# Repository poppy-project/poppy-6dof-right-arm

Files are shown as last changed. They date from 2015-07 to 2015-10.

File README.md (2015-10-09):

# Poppy Right Arm (WORK IN PROGRESS!)

Watch PoppyRightArm in action! :

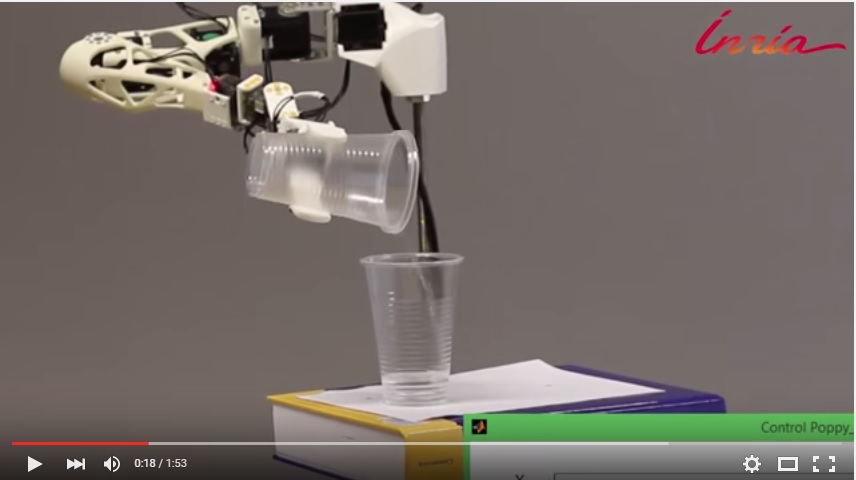
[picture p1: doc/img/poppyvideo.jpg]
Little red ridning hood (https://www.youtube.com/watch?v=47-JBuZhTWU&feature=youtu.be "Little red riding hood - Click to Watch!")


## [Documentation »](https://github.com/poppy-project/poppy-6dof-right-arm/blob/master/doc/README.md)
## [STL View »](doc/stl/PoppyRightArm.STL)

## Credit

The beginning of this project was inspired from the project [Poppy Humanoid](https://www.poppy-project.org/?lang=fr). This project was conceived to simulate an upper limb prostheses. In this [link](https://vimeo.com/134840606) you can watch an EMG control of Poppy Humanoid where this projectt will replace all Poppy humanoid to use only the part of interest, and in this other [link](https://github.com/joelortizsosa/EMG_Processing) you can dowload the software used in the video

This project is in charge of the research center [INRIA](http://www.inria.fr/centre/bordeaux) in collaboration of [INCIA](http://www.incia.u-bordeaux1.fr/)

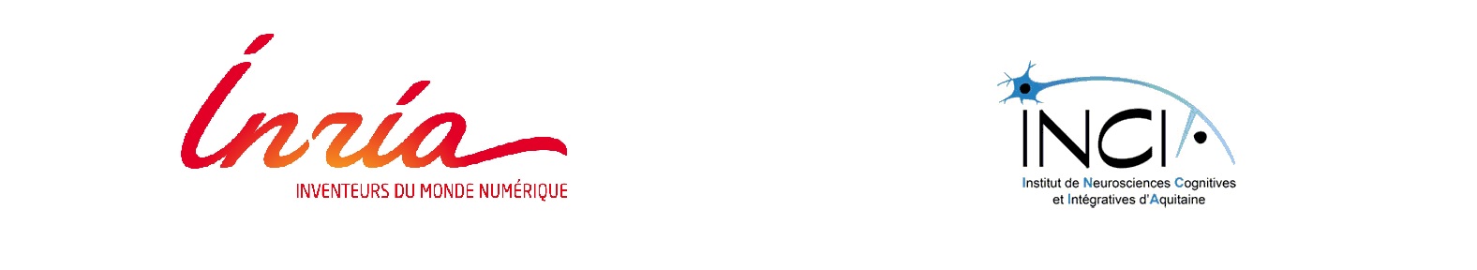
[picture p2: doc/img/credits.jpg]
credits


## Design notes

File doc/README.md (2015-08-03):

# Poppy Right Arm documentation

<p align="center">
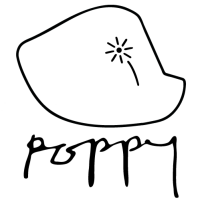
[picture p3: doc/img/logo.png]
Poppy_logo.

</p>

In this documentation you will find everything you need to assemble your own arm from scratch:

## [Assembly »]( https://github.com/poppy-project/poppy-6dof-right-arm/blob/master/doc/assembly.md)

In this section we explain, how you can assembly all the hadware ....

## [Electronic »]( https://github.com/poppy-project/poppy-6dof-right-arm/blob/master/doc/electronic.md)

In this section we explain, how you can power up all the motors ....

## [Software »]( https://github.com/poppy-project/poppy-6dof-right-arm/blob/master/doc/software.md)

In this section we explain, how you can install the creature necessary to control Poppy_Right_Arm, and we show some applications  ....

## [Common Bug »]( https://github.com/poppy-project/poppy-6dof-right-arm/blob/master/doc/common_Bug.md)

If you have any trouble when you execute your code, you can try watch this section ...

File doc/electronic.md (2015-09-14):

# About the Electronic

A small bit of electronic hacking is required for now. You need to power the XL-320 motors with 7.5V and the MX-28 with 12V.

The cables between motors have two purposes:

* Distribute alimentation to each motor
* Convey messages to each motor (ordering them to move or asking them for sensors values)

Thus the alimentation should be added between the USB2AX (that deals with communication aspects) and the motors.
To this end simply create the following card that can power both type of motors.

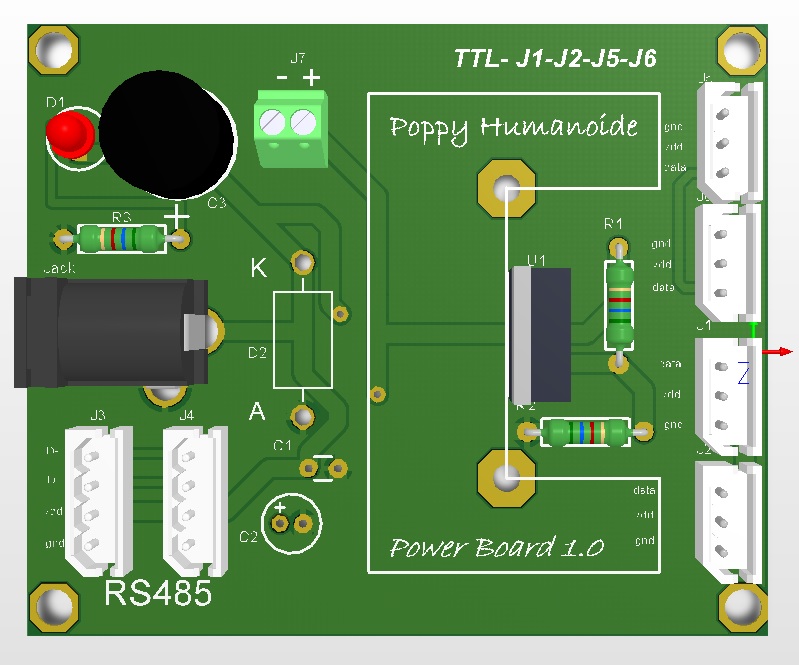
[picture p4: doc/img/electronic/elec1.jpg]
elec1


## Bill of Materials

| Description                   | Designator | Quantity |
| -----------------------------:|:----------:|:--------:|
| [CAP CER 0.1UF 50V RADIAL](http://fr.farnell.com/kemet/c320c104m5u5ta/condensateur-mlcc-z5u-100nf-50v/dp/1457658)      |    C1      |     1    |          
| [CAP ALUM 1.0UF 50V RADIAL](http://fr.farnell.com/nichicon/ukw1h010mdd1td/aluminum-electrolytic-capacitor/dp/1823811)     |    C2      |     1    |
| [Cap Aluminum Lytic 1000uF 25V](http://fr.farnell.com/panasonic-electronic-components/eca1ehg102/condensateur-elec-alu-1000uf-25v/dp/1848543) |    C3      |     1    |
| [Standard LED](http://fr.farnell.com/vishay/tlur4400/led-3mm-rouge/dp/1045372)                  |    D1      |     1    |
| [1N5822](http://fr.farnell.com/multicomp/1n5822/diode-schottky-3a-40v/dp/7429339)                        |    D2      |     1    |
| [Molex 22-03-5035](http://fr.farnell.com/molex/22-03-5035/embase-droite-2-5mm-3-voies/dp/9979620?ost=Molex+22-03-5035)              |   J1,J2    |     2    |
| [Molex 22-03-5045](http://fr.farnell.com/molex/22035045/embase-vertical-2-5mm-4-voies/dp/1104204?ost=Molex+22-03-5045)              |   J3,J4    |     2    |
| [Molex 53253-0370](http://fr.farnell.com/molex/53253-0370/embase-male-2-0mm-3-voies/dp/1756921?ost=Molex+53253-0370)              |   J5,J6    |     2    | 
| [CONN 2POS 1725656](http://fr.farnell.com/phoenix-contact/1725656/bornier-sur-ci-2v-2-54mm/dp/3041359?ost=Phoenix+Contact+1725656)             |    J7      |     1    |
| [CONN PWR JACK  PJ-202AH](http://fr.farnell.com/switchcraft/rapc712bk/connector-dc-power-jack-5a/dp/1617204?CMP=os_Google-FR_ProductDetail_Redirect)       |   JACK     |     1    |
| [Resistors 200Ohm 1/4W](http://fr.farnell.com/multicomp/mcmf0w4ff2000a50/metal-film-resistor-200-ohm-250mw/dp/1126948)         |    R1      |     1    |
| [Resistors 1KOhm 1/4W](http://fr.farnell.com/multicomp/mcmf0w4ff1001a50/metal-film-resistor-1kohm-250mw/dp/1126919)          |    R2      |     1    |
| [Resistors 430Ohm  1/4W](http://fr.farnell.com/multicomp/mcmf0w4ff4300a50/metal-film-resistor-430-ohm-250mw/dp/1129150)        |    R3      |     1    |
| [Adjuste Regulator LM317](http://fr.farnell.com/stmicroelectronics/lm317t/regulateur-ajust-1-2-37v-to-220/dp/9756027)       |    U1      |     1    |
| [H/SINK 6396B](http://fr.farnell.com/aavid-thermalloy/6396bg/dissipateur-to-220-218-5-6c-w/dp/1213472?ost=6396B)| TO-220 radiator |   1  |
The card design has been made in CircuitMaker, you can open the project in:

[https://workspace.circuitmaker.com/Account/Login?ReturnUrl=%2fProjects%2f5513C8C5-B3C1-4E83-8C02-FD9805562557] (https://workspace.circuitmaker.com/Account/Login?ReturnUrl=%2fProjects%2f5513C8C5-B3C1-4E83-8C02-FD9805562557)

But you need an account, you can create an account in this [link](http://www.circuitmaker.com/thank-you/#download), then you have access to project.

If you have your own PCB designer for make circuits, you can follow this schematic:

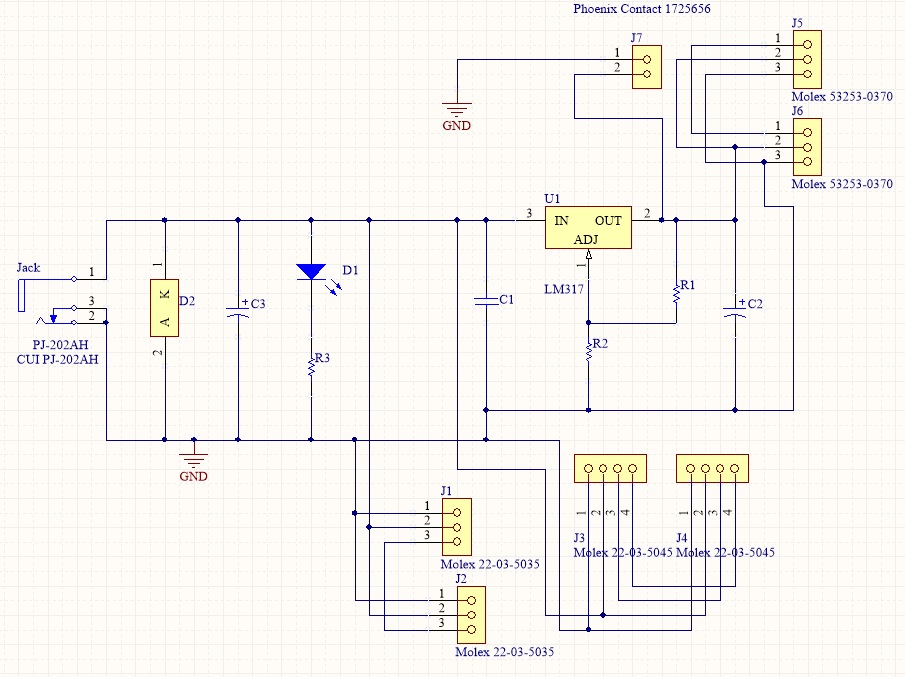
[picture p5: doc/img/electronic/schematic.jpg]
schematic


## [Software »]( https://github.com/poppy-project/poppy-6dof-right-arm/blob/master/doc/software.md)

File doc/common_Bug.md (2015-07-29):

# Error in voltage

The voltage for the XL-320 is configured at 7.4V in pypot, if the source power has more voltage, pypot detect:

  **NotImplementedError**

The dynamixel XL-320 supports up to 8 volts, so we can modify the library to correct this error, because when this 
error appears, the motors stop working.

we need to find the file error.py, usually found in:

 *C:\Python27\Lib\site-packages\pypot\dynamixel\error.py*
 
Then we comment the line 52, and we add the sentence "pass", like the image below:

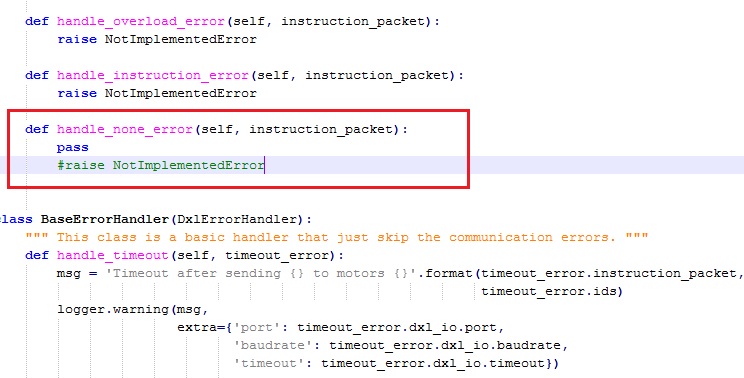
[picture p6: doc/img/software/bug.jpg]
bug


With this modification we can control the motors without any inconvenience

## [Home »] (https://github.com/joelortizsosa/Poppy_Right_Arm_Creature/blob/master/doc/README.md)

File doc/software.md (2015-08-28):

# About the Software

## Install Creature

you can donwload the creature in this [link](https://github.com/poppy-project/poppy-6dof-right-arm/archive/master.zip).To make the installation (in windows xp,7,8), It's necessary load  the command-line interpreter on Windows and then 
you need to be located in the folder of the creature:

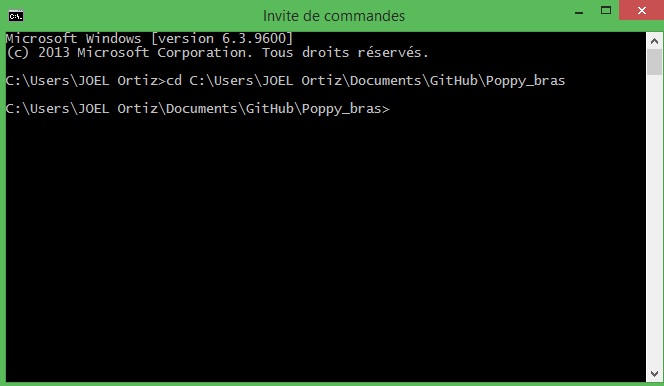
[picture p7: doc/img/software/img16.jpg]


Then you can install the library as follows

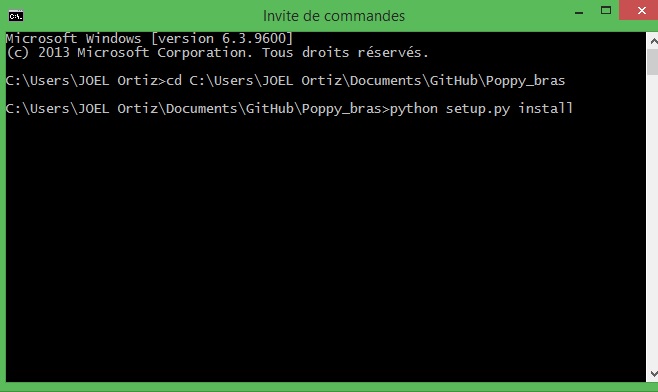
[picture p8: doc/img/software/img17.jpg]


*If you dont have python and the software necessay already installed, you can follow these [instructions](https://forum.poppy-project.org/t/poppy-on-windows-all-you-need-to-do/392)*

## Configuration of *.JSON

As the gripper of the arm can be configured to add different degrees of freedom, it is necessary to disable / enable the motors to be used. To do this you need to modify the configuration file, located at:

*C:\Python27\Lib\site-packages\poppy_right_arm-1.0.0-py2.7.egg\poppy_right_arm\configuration\poppy_right_arm.json*

Then you can open this file with the Notepad

* if you write "true", the motor will be disabled.

* if you write "false", the motor will be enabled.

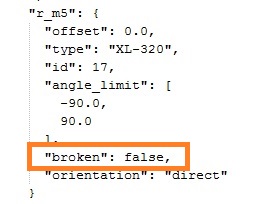
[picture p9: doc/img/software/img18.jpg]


> *Note: change the file. * json in Poppy_Right_Arm not cause bug in any others creatures*

Once these parameters are defined, now we can use the creature.

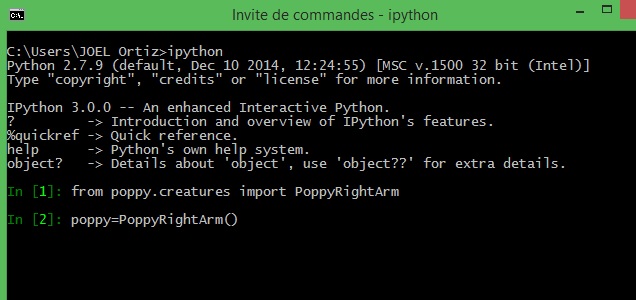
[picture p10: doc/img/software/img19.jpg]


## Python Server

To control the Poppy_Right_Arm from another software such as Matlab, you must create a server in python that can handle all the motors remotely.

We can start an HTTP server permitting the remote access of  Poppy_Right_Arm creature. In this [link](https://github.com/poppy-project/pypot/blob/master/samples/notebooks/Accessing%20pypot%20REST%20API%20through%20HTTP%20requests.ipynb) you can find one explanation. Extra [information](https://github.com/poppy-project/pypot/blob/master/REST-APIs.md).

**Note: Poppy_Right_Arm creature use a software architecture style for building scalable web services (REST-API)*

we implemented a server, with the ideal setting to control the Poppy_Right_Arm. You can see the code in this [link] (https://github.com/poppy-project/poppy-6dof-right-arm/blob/master/applications/HTTP_server/Poppy_Right_Arm_Server.py)
To execute the server it's necessary load  the command-line interpreter and to be located in the folder of the code, then you put this code:

**python Poppy_Right_Arm_Server.py**

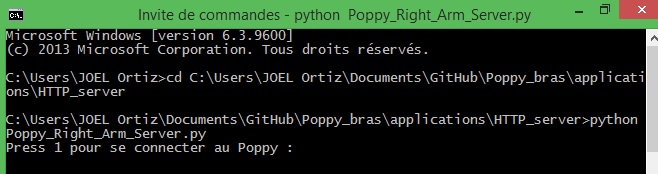
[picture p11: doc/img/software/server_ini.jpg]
server_ini


*Note: if you have saved the code with another name, it is necessary to run with that name*

## Matlab Control

With the python server we can do different applications, for example we used matlab to calculate the inverse kinematics to control the arm, for do it, we use the calcule of this [link](https://forum.poppy-project.org/t/cinematique-inverse-bras-de-poppy/1306)

There are many software with [REST API](https://en.wikipedia.org/wiki/Representational_state_transfer) support, Matlab only support REST API from 2014 version, but we can use the HTTP protocol. The HTTP protocol implemented in Matlab is very basic, you can download an improved version in this [link](http://www.mathworks.com/matlabcentral/fileexchange/35693-urlread2)

We did a client in matlab that you can download from this [link](https://github.com/poppy-project/poppy-6dof-right-arm/raw/master/applications/Matlab_client/Matlab_client.rar). This client can control the Poppy_Right_Arm using the inverse kinematics, only you have to press the boton "Connect" and then move the sliders of each axe.

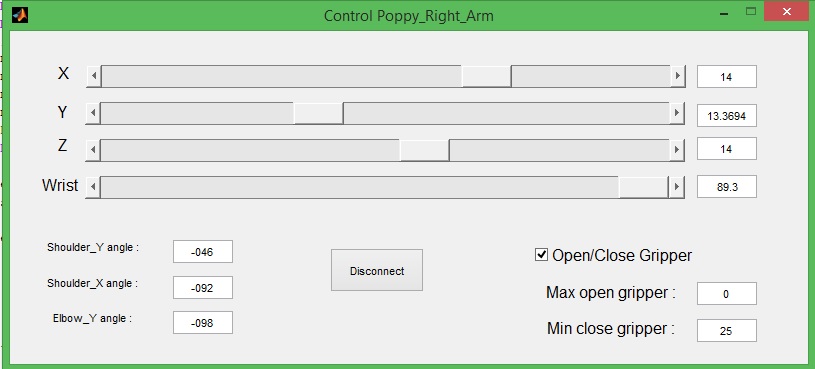
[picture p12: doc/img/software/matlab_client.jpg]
matlab_client


We developed the same sotware in python, using PyQT4, you can access in this [link](https://github.com/joelortizsosa/Inverse-Kinematic-Python)

## [Home »] (https://github.com/poppy-project/poppy-6dof-right-arm/blob/master/doc/README.md)

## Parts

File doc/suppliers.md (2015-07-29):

# List of Suppliers

## Robotics

### OLLO

* Ollo rivets: http://www.generationrobots.com/en/401870-ollo-rivet-set-ors-10.html?search_query=OLLO&results=11

### Dynamixel

* XL320: http://www.generationrobots.com/en/401692-dynamixel-xl-320-servo-motor.html
* MX-28: http://www.generationrobots.com/fr/401080-servomoteur-dynamixel-mx-28t.html?search_query=MX-28T&results=15

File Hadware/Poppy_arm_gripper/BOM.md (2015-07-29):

| Part Name       | Quantity |   Note   |
| ---------------:|:--------:|:--------:|
| Shift_one_side  |    2     |          |
| forearm         |    1     |          |
| morceau_1       |    1     |          |
| morceau_2       |    1     |          |
| shoulder        |    1     |          |
| supp_gripper    |    1     |          |
| supp_1          |    2     |          |
| supp_2          |    1     |          |
| supp_3          |    1     | Optional |
| supp_bras_droit |    1     |          |
| supp_for_table  |    1     |          |
| upper_arm       |    1     |          |

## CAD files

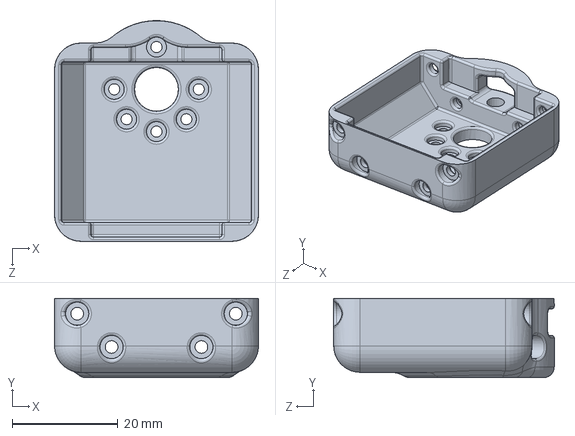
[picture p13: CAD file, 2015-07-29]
Hadware/Poppy_arm_gripper/Components/shoulder.SLDPRT
38.6 x 15.0 x 41.7 mm

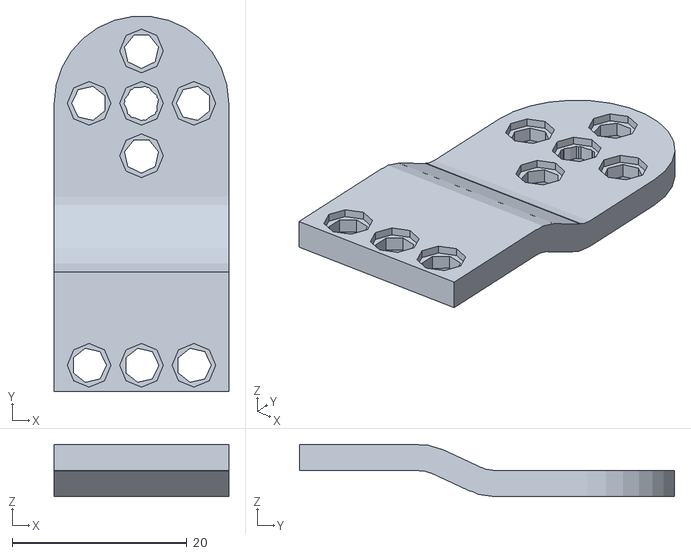
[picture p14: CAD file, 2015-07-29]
Hadware/Poppy_arm_gripper/Components/STL/shift_one_side.stl
20.0 x 42.9 x 6.00

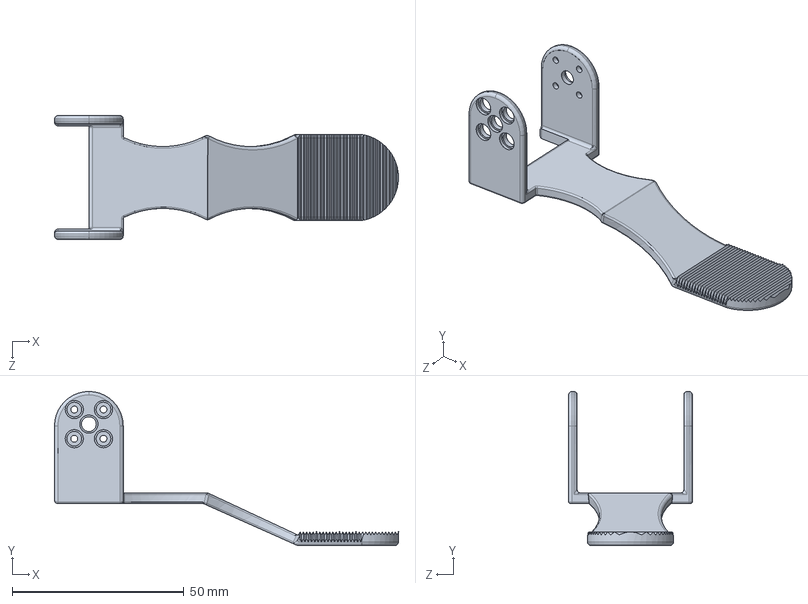
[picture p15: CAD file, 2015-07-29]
Hadware/Poppy_arm_gripper/Components/morceau_2.SLDPRT
100.0 x 44.8 x 36.0 mm

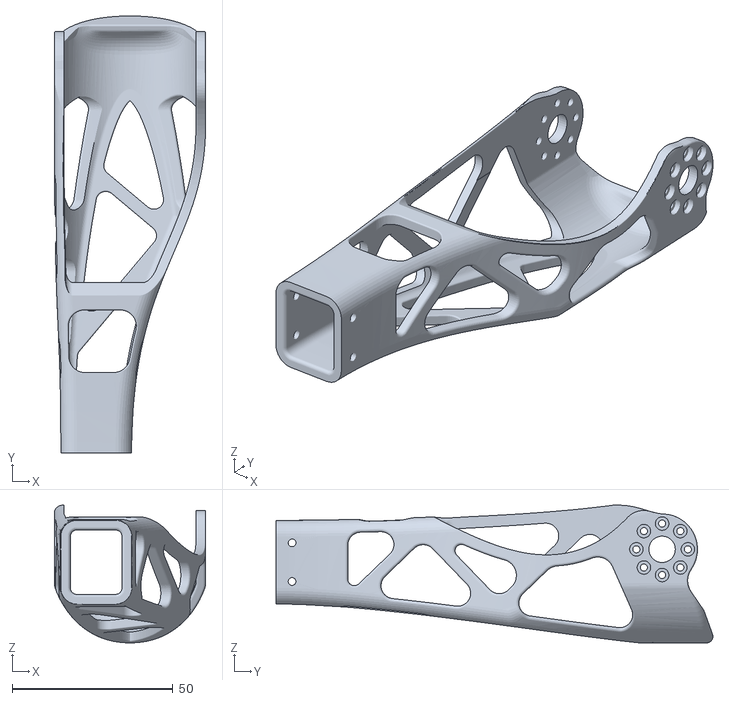
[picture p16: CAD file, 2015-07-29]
Hadware/Poppy_arm_gripper/Components/STL/forearm.STL
47.0 x 135.8 x 42.8

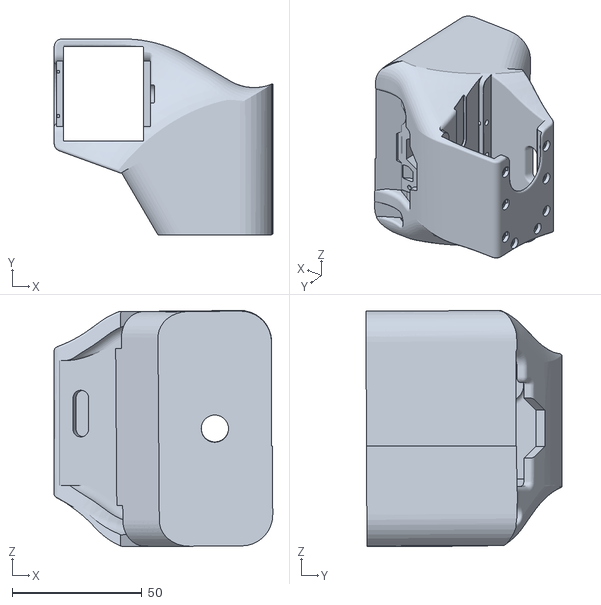
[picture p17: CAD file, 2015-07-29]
Hadware/Poppy_arm_gripper/Components/STL/support_Bras_droit_mod1.STL
84.2 x 75.6 x 90.9

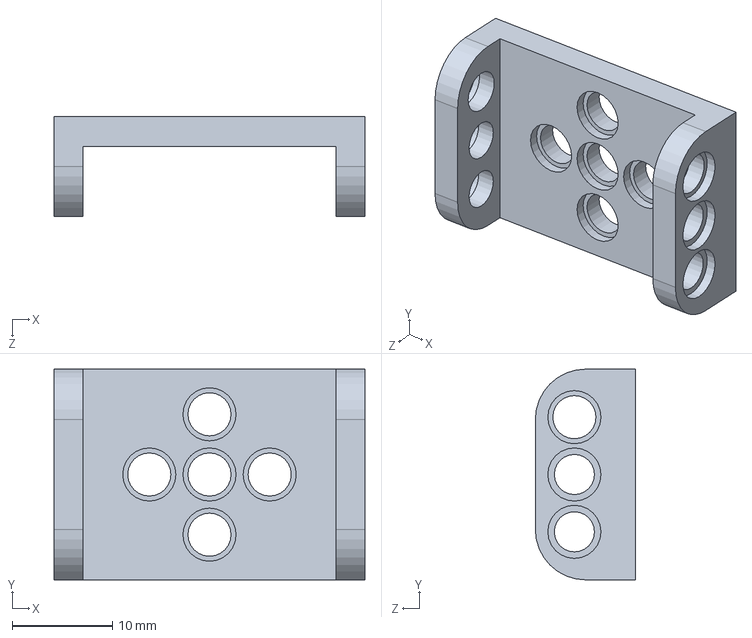
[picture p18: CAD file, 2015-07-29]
Hadware/Poppy_arm_gripper/Components/supp_1.SLDPRT
31.0 x 21.0 x 10.0 mm

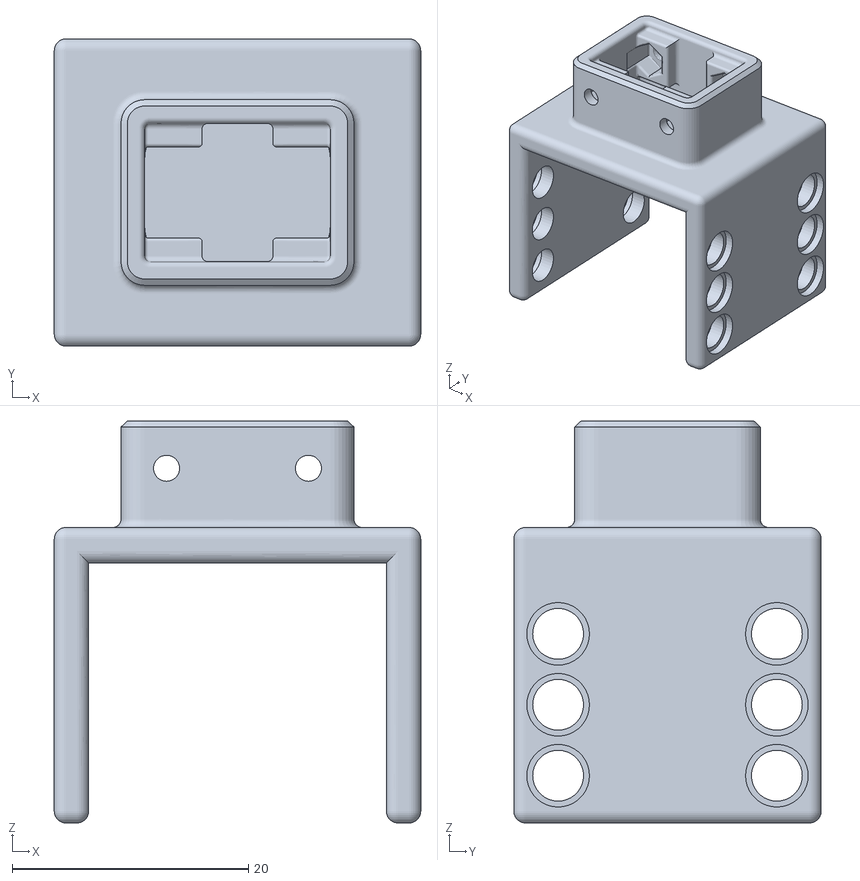
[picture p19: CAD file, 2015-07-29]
Hadware/Poppy_arm_gripper/Components/STL/support_gripper.STL
31.0 x 26.0 x 34.0

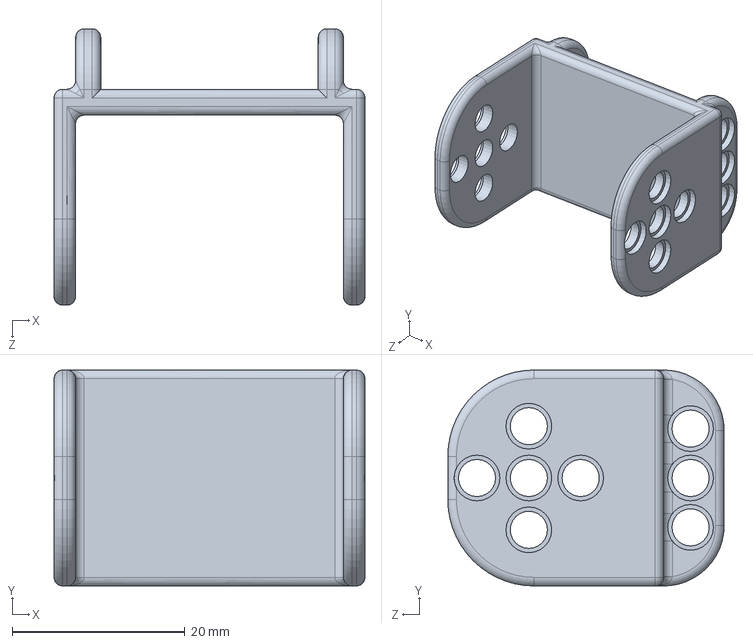
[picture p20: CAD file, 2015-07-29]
Hadware/Poppy_arm_gripper/Components/supp_3.SLDPRT
36.0 x 25.0 x 32.0 mm

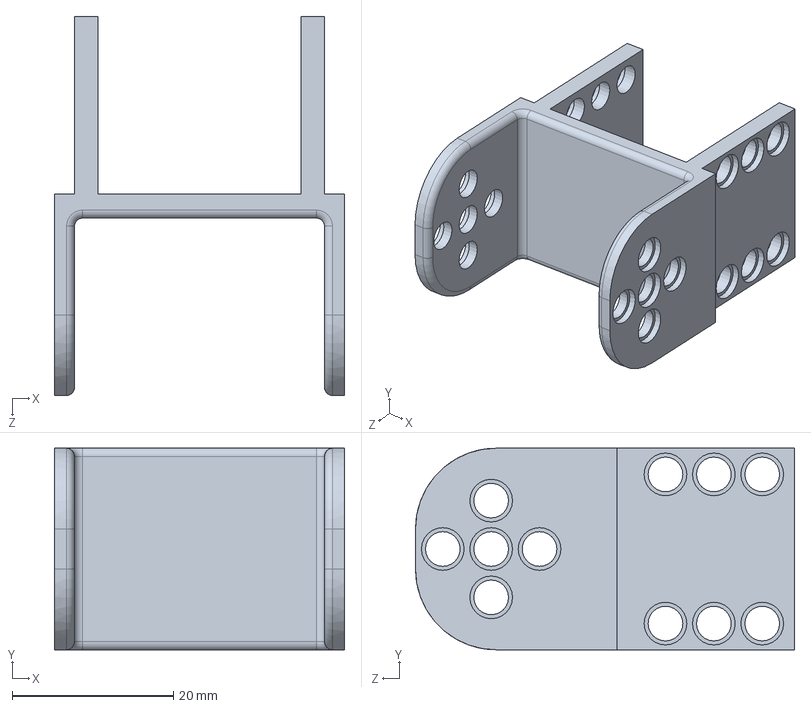
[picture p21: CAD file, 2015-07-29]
Hadware/Poppy_arm_gripper/Components/supp_2.SLDPRT
36.0 x 25.0 x 47.0 mm

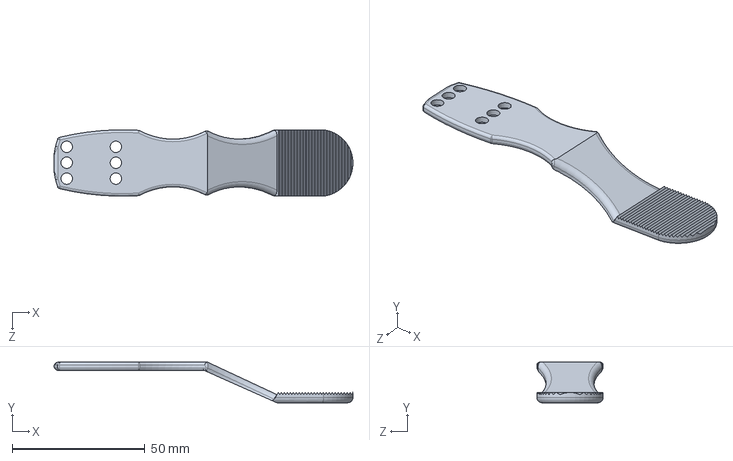
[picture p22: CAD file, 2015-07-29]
Hadware/Poppy_arm_gripper/Components/morceau_1.SLDPRT
112.6 x 15.3 x 25.0 mm

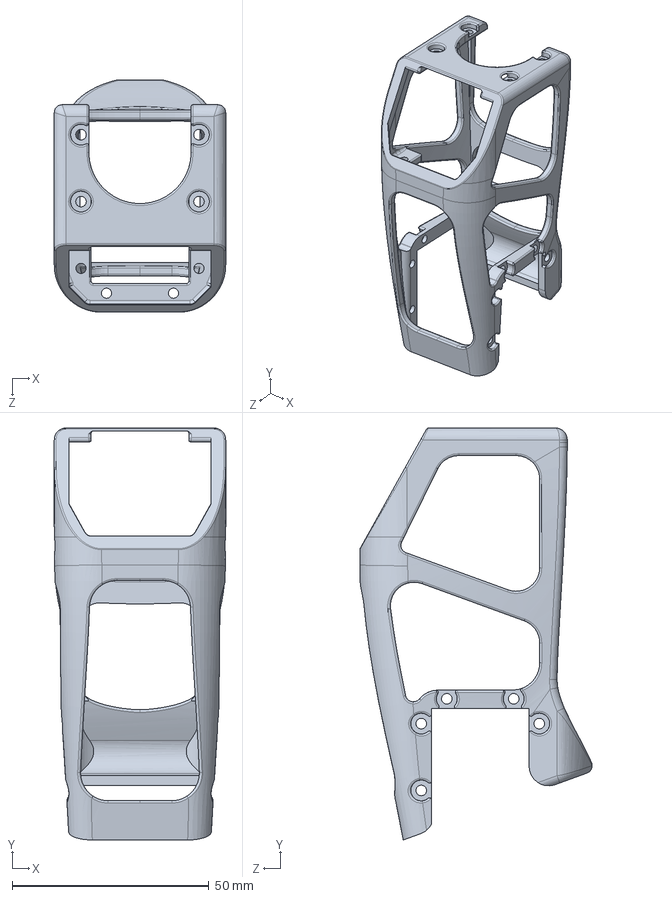
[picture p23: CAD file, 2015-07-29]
Hadware/Poppy_arm_gripper/Components/upper_arm.SLDPRT
43.6 x 104.7 x 59.1 mm

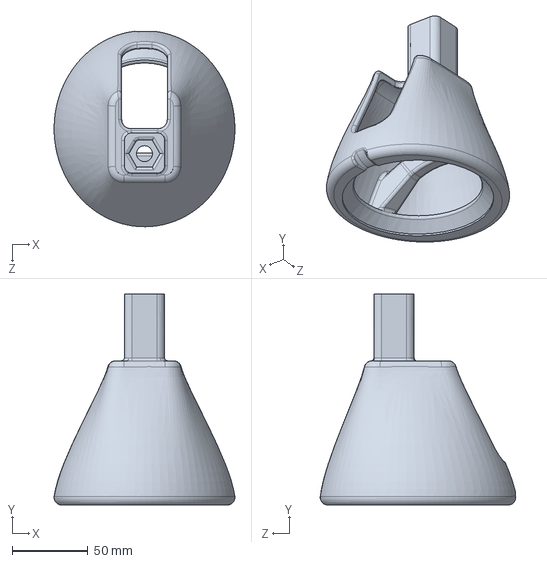
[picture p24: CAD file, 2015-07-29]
Hadware/Poppy_arm_gripper/Components/support_for_table.SLDPRT
119.1 x 139.0 x 128.8 mm

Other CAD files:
Hadware/Poppy_arm_gripper/Components/STL/morceau_1.STL
Hadware/Poppy_arm_gripper/Components/STL/morceau_2.STL
Hadware/Poppy_arm_gripper/Components/STL/shoulder.STL
Hadware/Poppy_arm_gripper/Components/STL/supp_1.STL
Hadware/Poppy_arm_gripper/Components/STL/supp_2.STL
Hadware/Poppy_arm_gripper/Components/STL/supp_3.STL
Hadware/Poppy_arm_gripper/Components/STL/support_for_table.STL
Hadware/Poppy_arm_gripper/Components/STL/upper_arm.STL

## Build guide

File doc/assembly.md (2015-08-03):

# Step by Step Assembly

## BOM

For building a Poppy right Arm, you will need:

* 5x robotis [XL-320] (http://www.generationrobots.com/en/401692-dynamixel-xl-320-servo-motor.html?search_query=OLLO&results=23)
* 10x [XL cable](http://www.generationrobots.com/en/402090-3p-130-mm-cables-for-xl-servos-x5.html)
* 2x [USB2AX] (http://www.generationrobots.com/en/401584-usb2ax-for-dynamixel-servos.html?search_query=usb2aX&results=5)
* 4x robotics [MX-28] (http://www.generationrobots.com/en/401080-dynamixel-mx-28t-actuator-robotis.html?search_query=MX-28T&results=15)
* 2x HN07-I101 [Horn](http://www.generationrobots.com/en/400939-hn07-i101-horn-and-bearing-set-for-dynamixel-actuators-robotis.html)
* 1x FR07-H101K [Set] (http://www.generationrobots.com/en/400917-fr07-h101k-set-robotis.html?search_query=FR07-H101K&results=2)
* 1x [TTL cable](http://www.generationrobots.com/en/401739-3p-cable-set-bcs-3p01-for-dynamixel-servo-motors.html?search_query=mx+cable&results=336)
* 1x small electronic board (see the [electronic section](electronic.md))
* 1x [Power Supply 12V - 5A] (http://www.trossenrobotics.com/p/power-supply-12vdc-5a.aspx)
* the 3D printed parts: [STL] (https://github.com/joelortizsosa/Poppy_bras_Creatures/releases) [BOM](https://github.com/joelortizsosa/Poppy_bras_Creatures/blob/master/Hadware/Poppy%20bras%20prehenseur/BOM.md)
* 1x [threaded shaft](http://www.leroymerlin.fr/v3/p/produits/tige-filetee-en-acier-zingue-long-1-m-x-diam-10-mm-e54322) D:10mm L: min 45 cm
* 4x [Hex Nut](http://www.vis-express.fr/fr/ecrous-inox-a2-hu/19735-ECROU-HEXAGONAL-M10-INOX-DACROMET-8425001057.html) D:10 mm
* 1x [OLLO Pulley-L](http://www.generationrobots.com/en/401871-ollo-pulley-l-gray-5pcs.html?search_query=OLLO&results=23) and their rivets
* many [OLLO rivets](http://www.generationrobots.com/en/401870-ollo-rivet-set-ors-10.html)
* 1x [OLLO Tool](http://www.generationrobots.com/en/401872-ollo-tool.html)
* 1x[100mm with lever arm suction pad](http://www.ventouses-soufflets.com/ventouses-avec-levier-d-appui/54-ventouse-100mm-avec-levier-d-appui-et-avec-patte-de-fixation-noire.html)
* 2x M5 nuts
* 2X M5x20mm screws
* 4x Bolt PHS M2x6 
* 4x N1 Nut M2 

### Visserie Optional:
* 1x Wrench Bolt M2.5*6 (200 pcs)
* 1x Nut M2.5 (400 pcs)

## Assembling your robot

## Step 1

First for assambly the poppy right arm we can use poppy basic arms [Doc] (https://github.com/poppy-project/Poppy-basic-arms/blob/master/doc/right_arm_assembly_instructions.md)

## Step 2
Mount the arm of step 1, motor MX-28, FR07 and threaded shaft on the 3D printed suppport.

Always align the horn with the motor before assembling them (red circle)

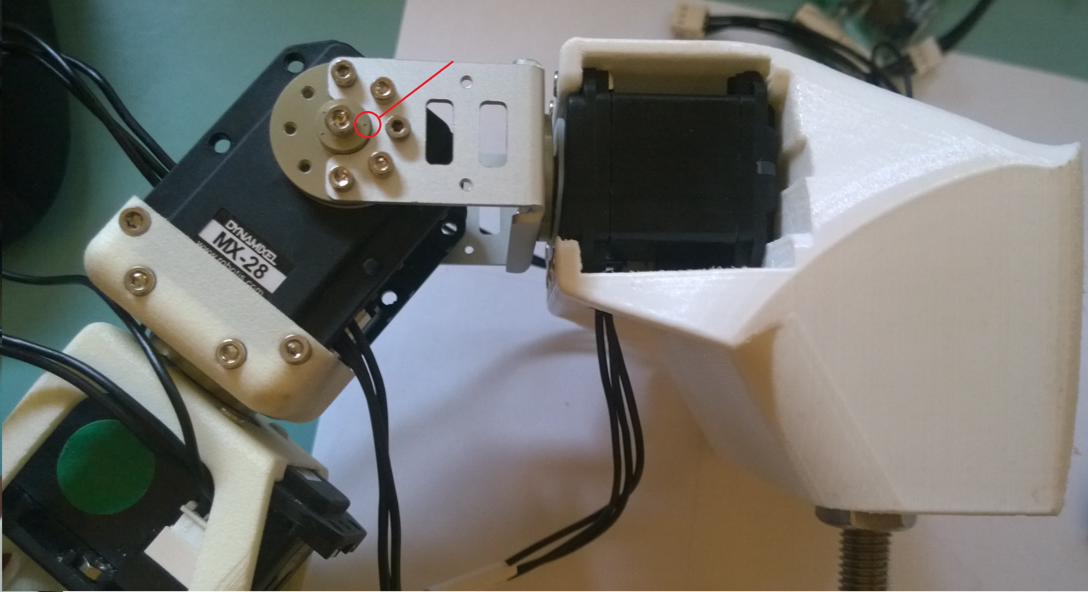
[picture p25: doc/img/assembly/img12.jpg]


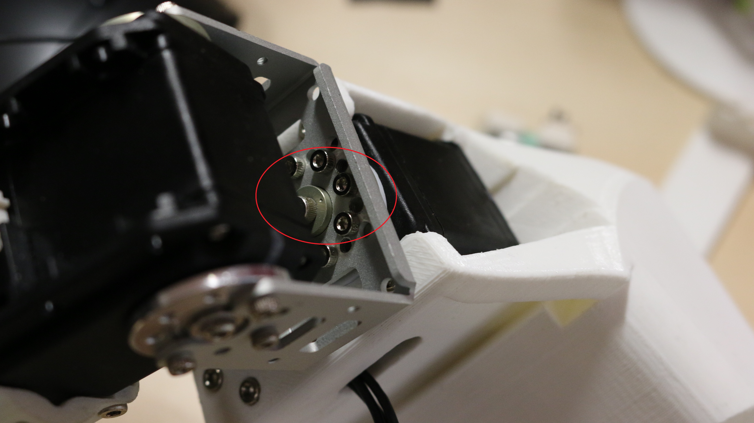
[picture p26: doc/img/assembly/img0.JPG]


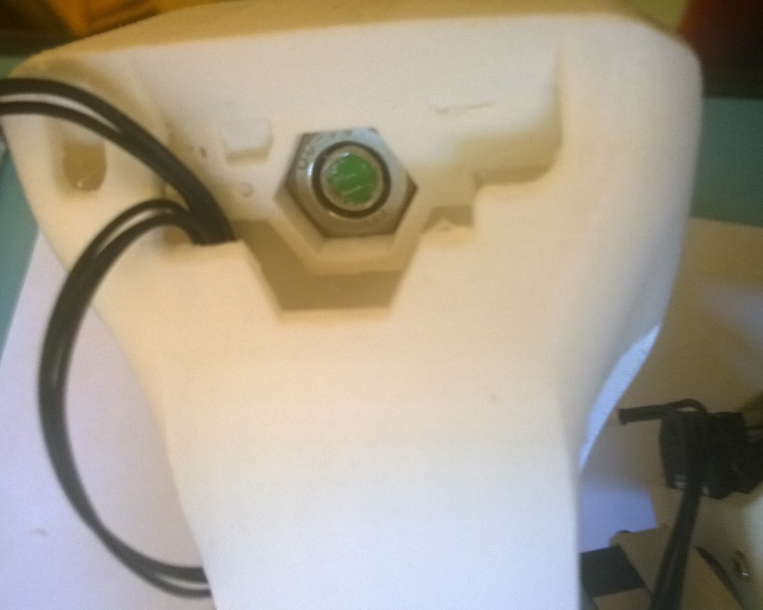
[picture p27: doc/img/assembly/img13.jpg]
step2_2


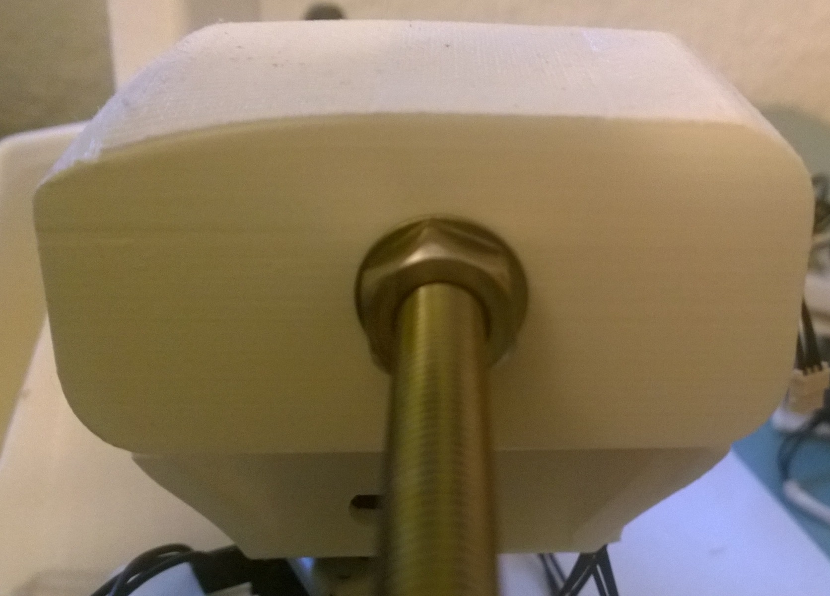
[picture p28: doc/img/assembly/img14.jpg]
step2_3


## Step 3

Mount step 2 in the support for table.

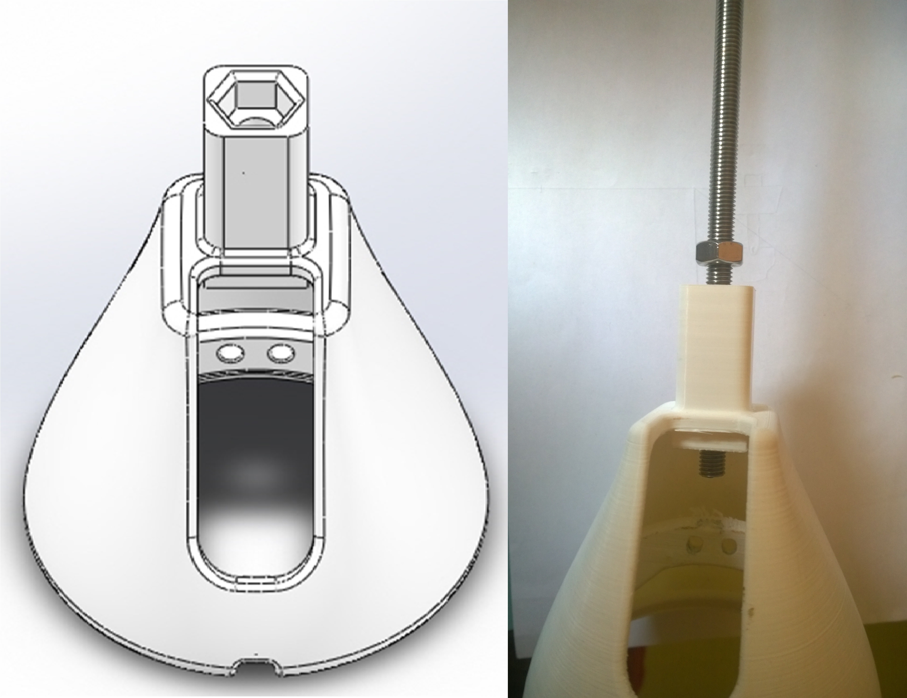
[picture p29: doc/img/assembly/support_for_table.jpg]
step3_1


## Step 4

Mount the suction pad inside the support for table

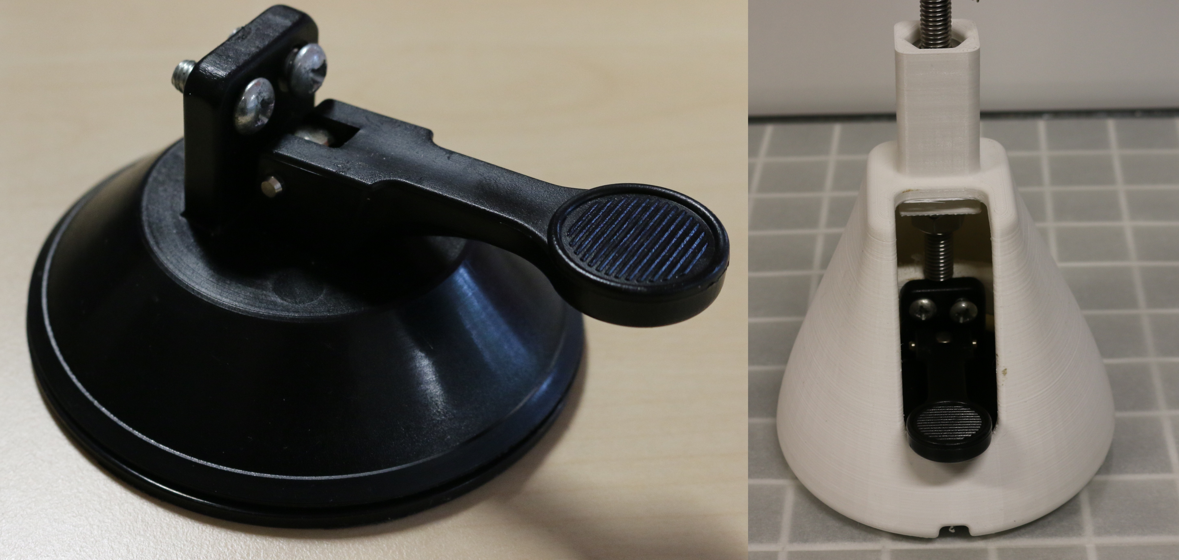
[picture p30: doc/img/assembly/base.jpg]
step4_1


## Step 5

Now you just need to mount the gripper, for do it, you have 3 possibilities each one gives the robot an additional degree of freedom.

3 degree of freedom without taking into account pronation and supination

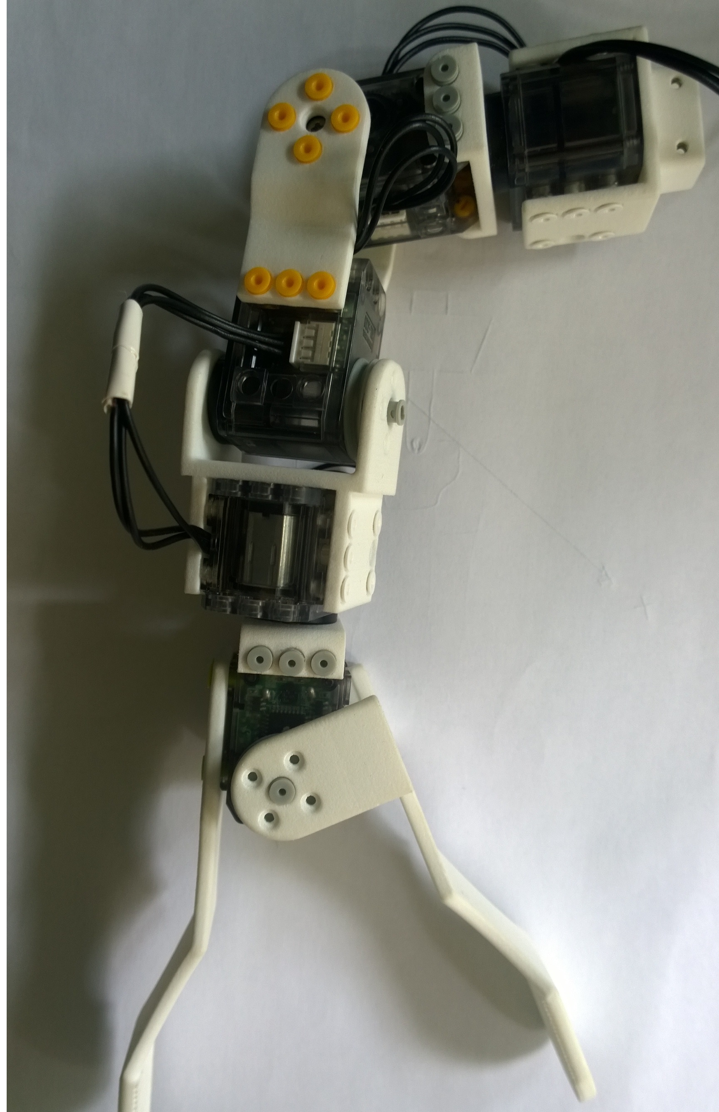
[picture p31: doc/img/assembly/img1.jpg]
step5_1


To mount some pieces you need the OLLO Pulley, you can watch how connect each OLLO Pulley [slow motion](https://vimeo.com/125704291).

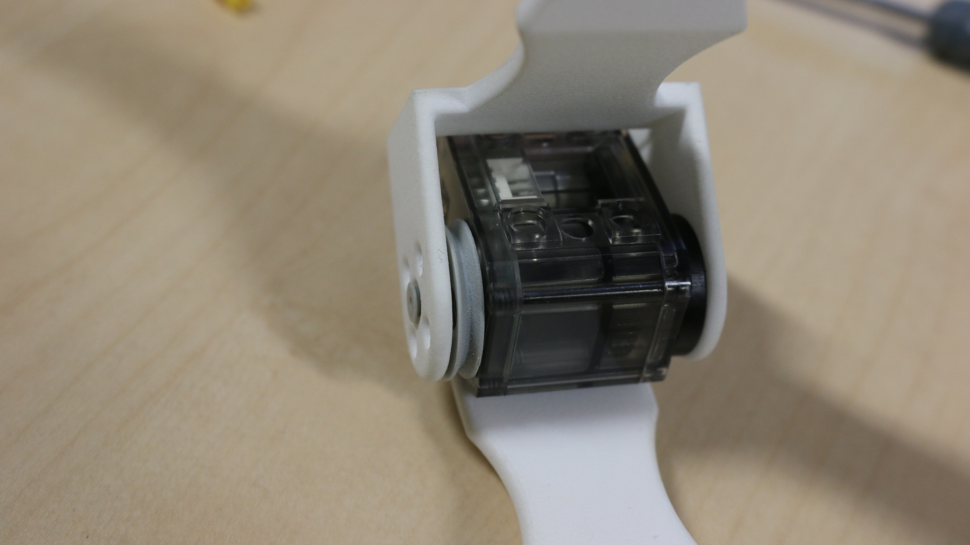
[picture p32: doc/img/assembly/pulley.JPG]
step5_2


## Step 6
To mount each piece you need many rivets,You can look at the following pictures how you can mount it.

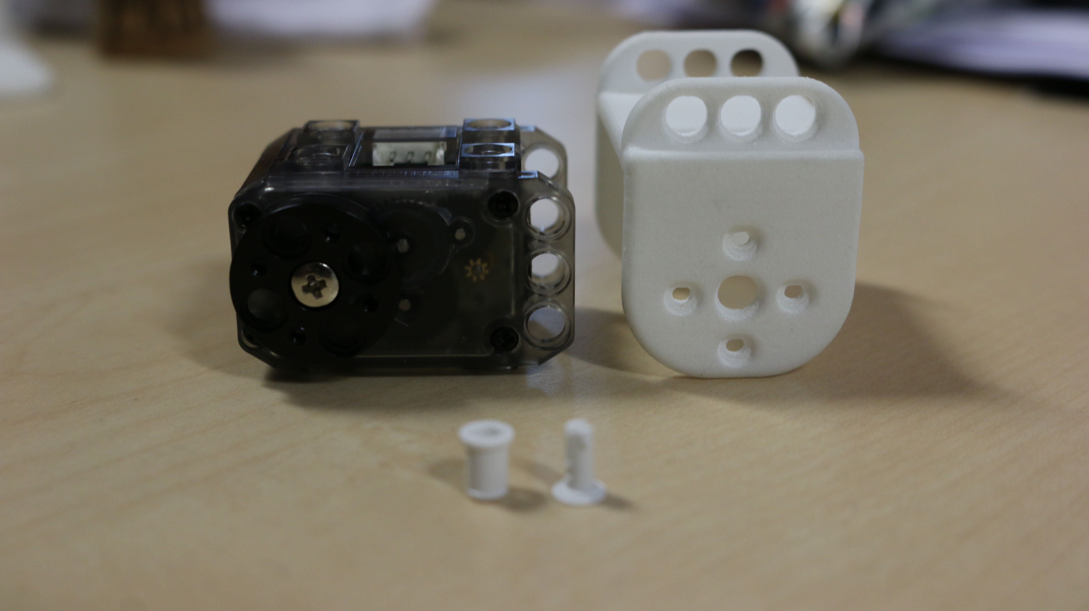
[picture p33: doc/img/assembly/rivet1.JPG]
step6_1


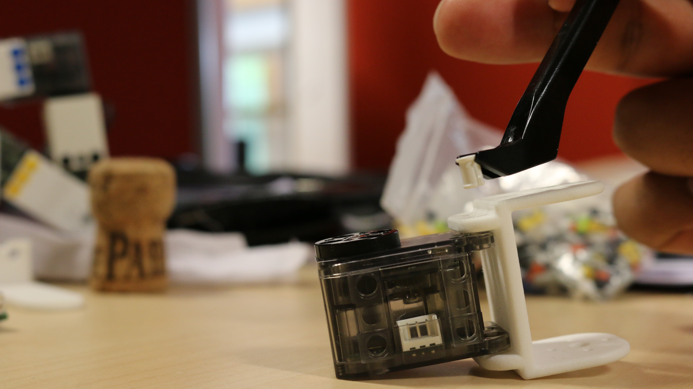
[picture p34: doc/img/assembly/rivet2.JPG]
step6_2


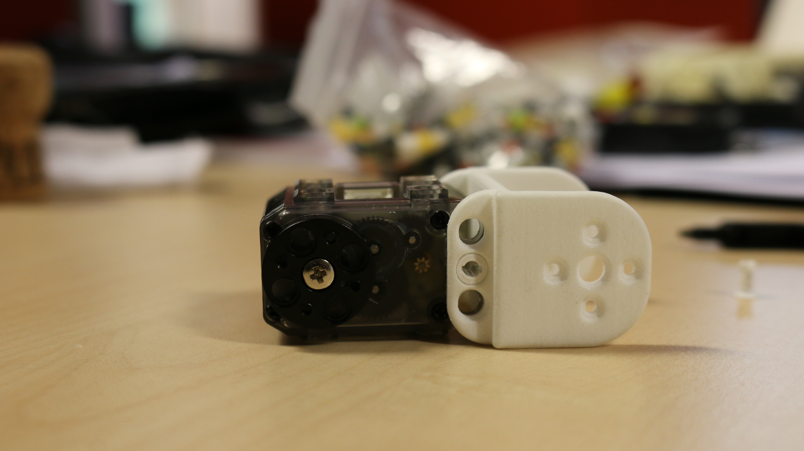
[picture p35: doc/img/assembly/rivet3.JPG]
step6_3


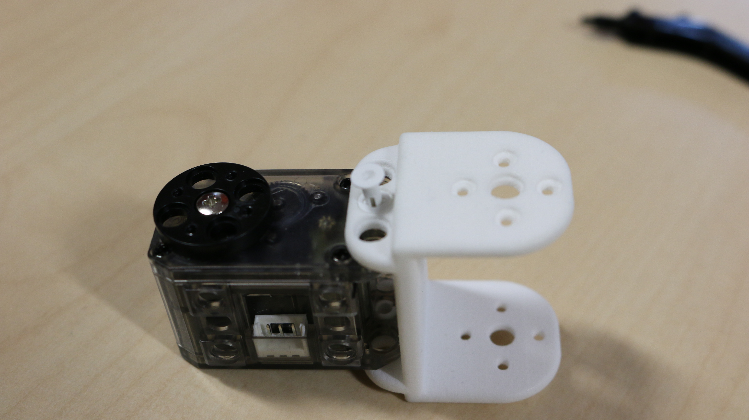
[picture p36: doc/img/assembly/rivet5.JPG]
step6_5


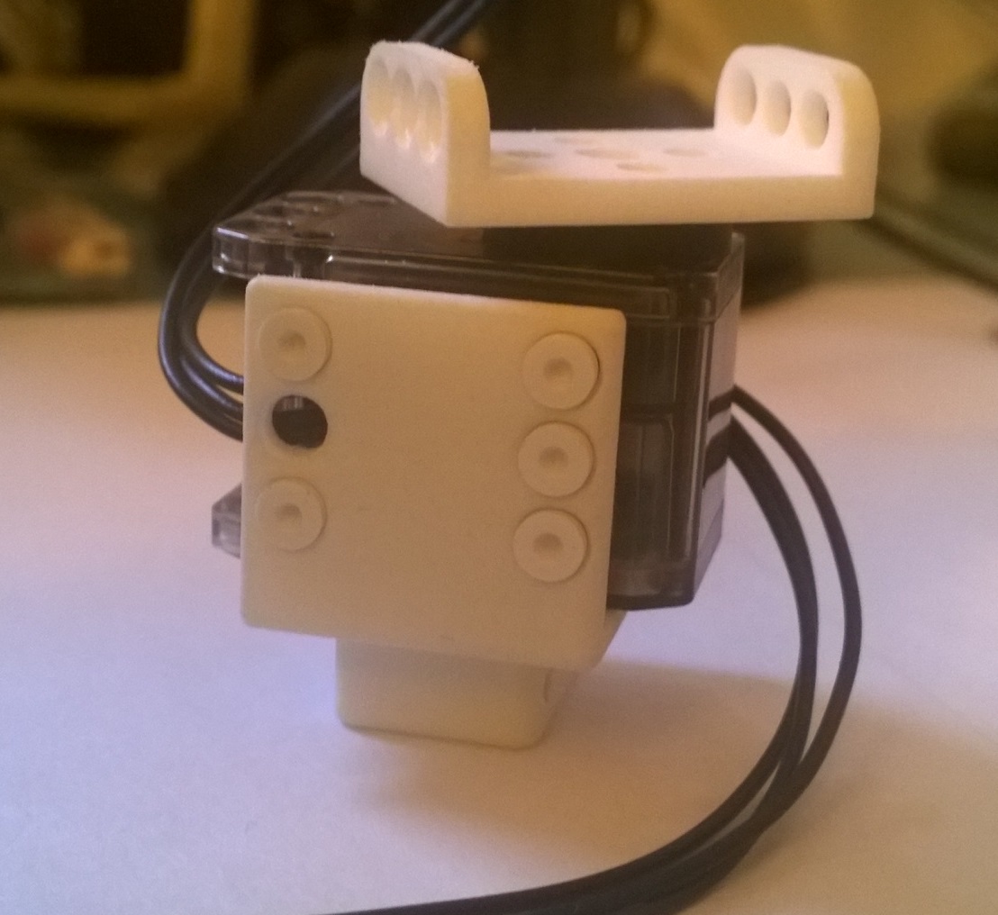
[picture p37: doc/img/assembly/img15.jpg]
step6_6


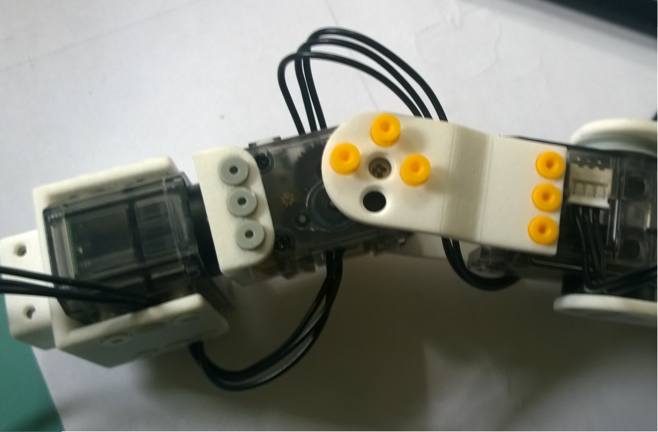
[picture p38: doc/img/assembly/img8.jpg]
step6_7


## Finally ...

<p align="center">

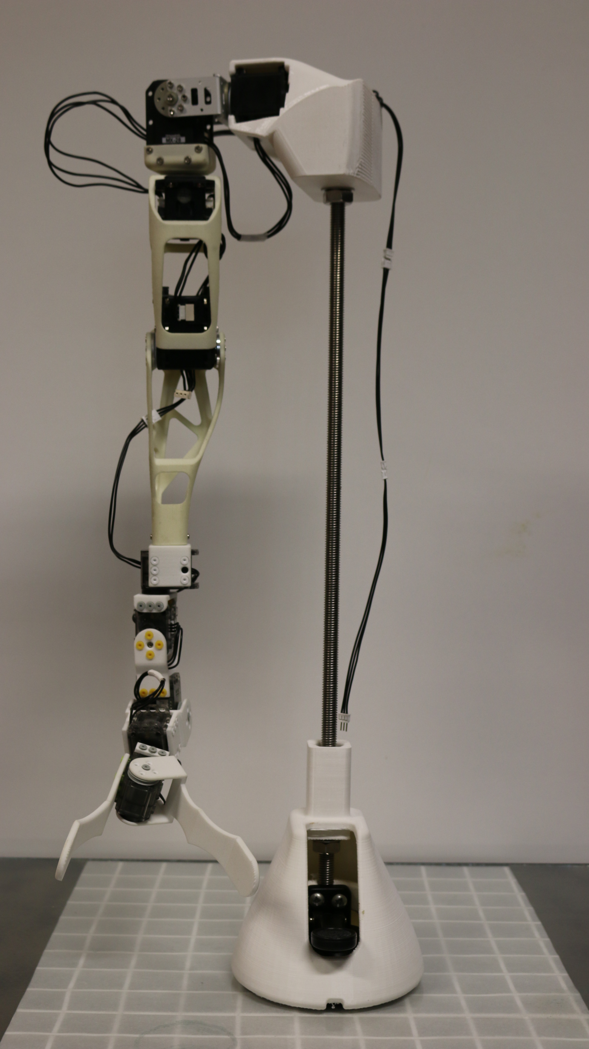
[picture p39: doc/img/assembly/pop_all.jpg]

</p>

## [Electronic »]( https://github.com/poppy-project/poppy-6dof-right-arm/blob/master/doc/electronic.md)

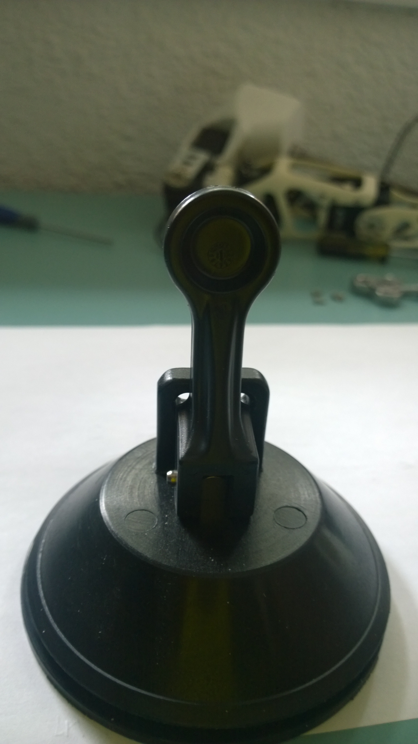
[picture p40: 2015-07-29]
doc/img/assembly/img3.jpg

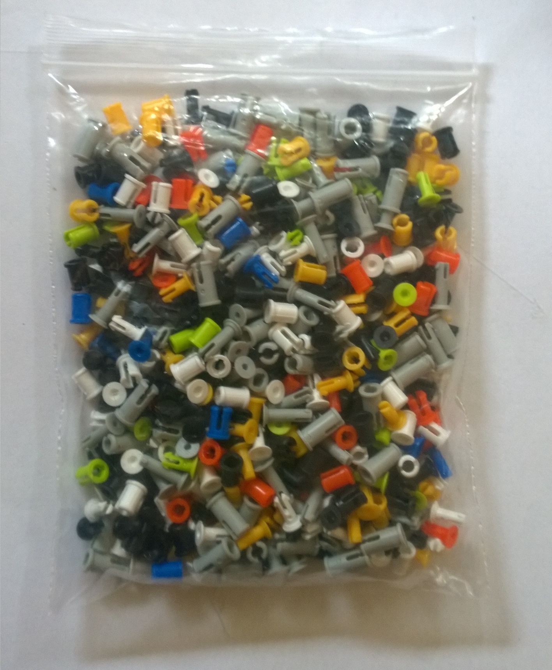
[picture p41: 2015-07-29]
doc/img/assembly/img9.jpg

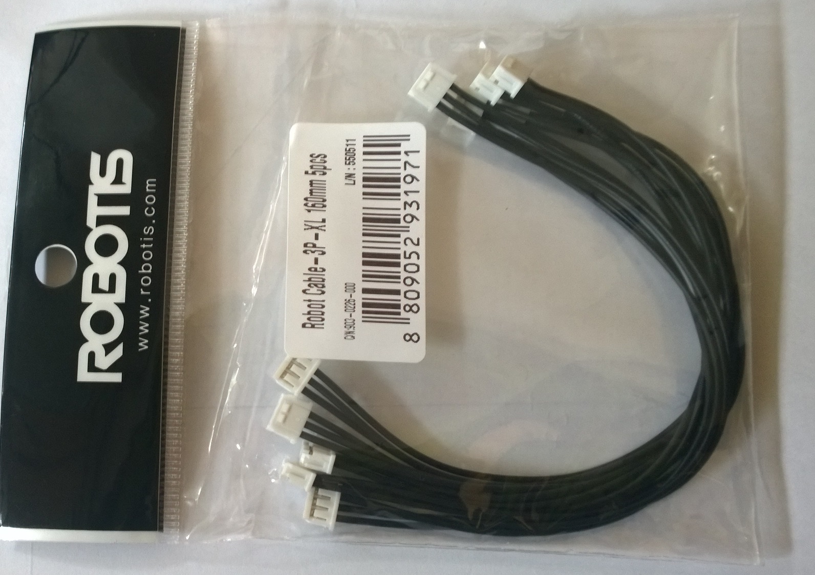
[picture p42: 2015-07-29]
doc/img/assembly/img10.jpg

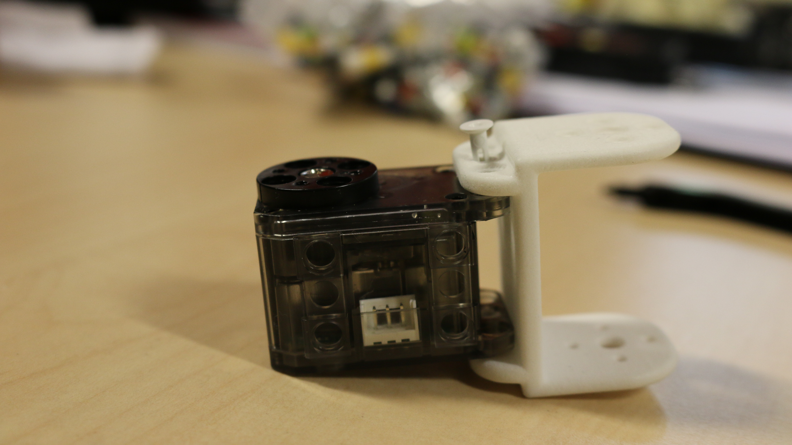
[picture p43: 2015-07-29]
doc/img/assembly/rivet4.JPG

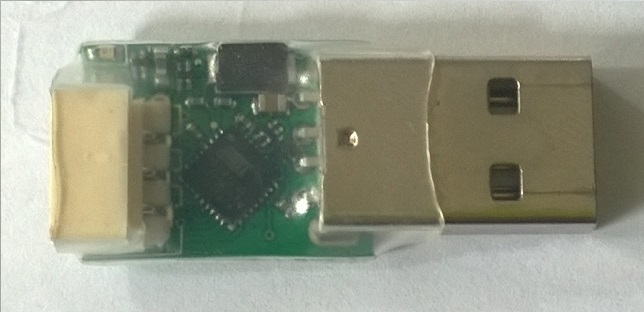
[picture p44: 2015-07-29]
doc/img/assembly/img5.jpg
